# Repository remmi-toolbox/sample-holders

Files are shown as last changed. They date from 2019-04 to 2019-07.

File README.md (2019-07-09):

# About sample-holders
This contains 3D print files for mouse brain holders of various sizes. Additional files for other types of tissue and phantom holders may be added in the near future. Designs were created by Dong Kyu Kim (dong.kyu.kim@vanderbilt.edu) and Mark Does (mark.does@vanderbilt.edu). Work is supported by NIH R01EB019980.

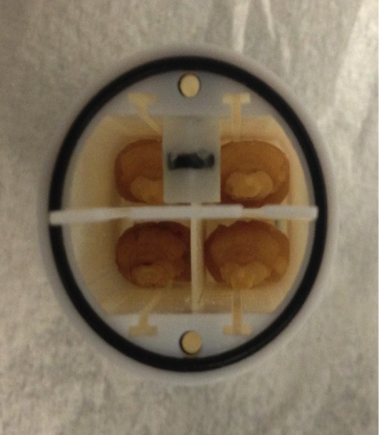
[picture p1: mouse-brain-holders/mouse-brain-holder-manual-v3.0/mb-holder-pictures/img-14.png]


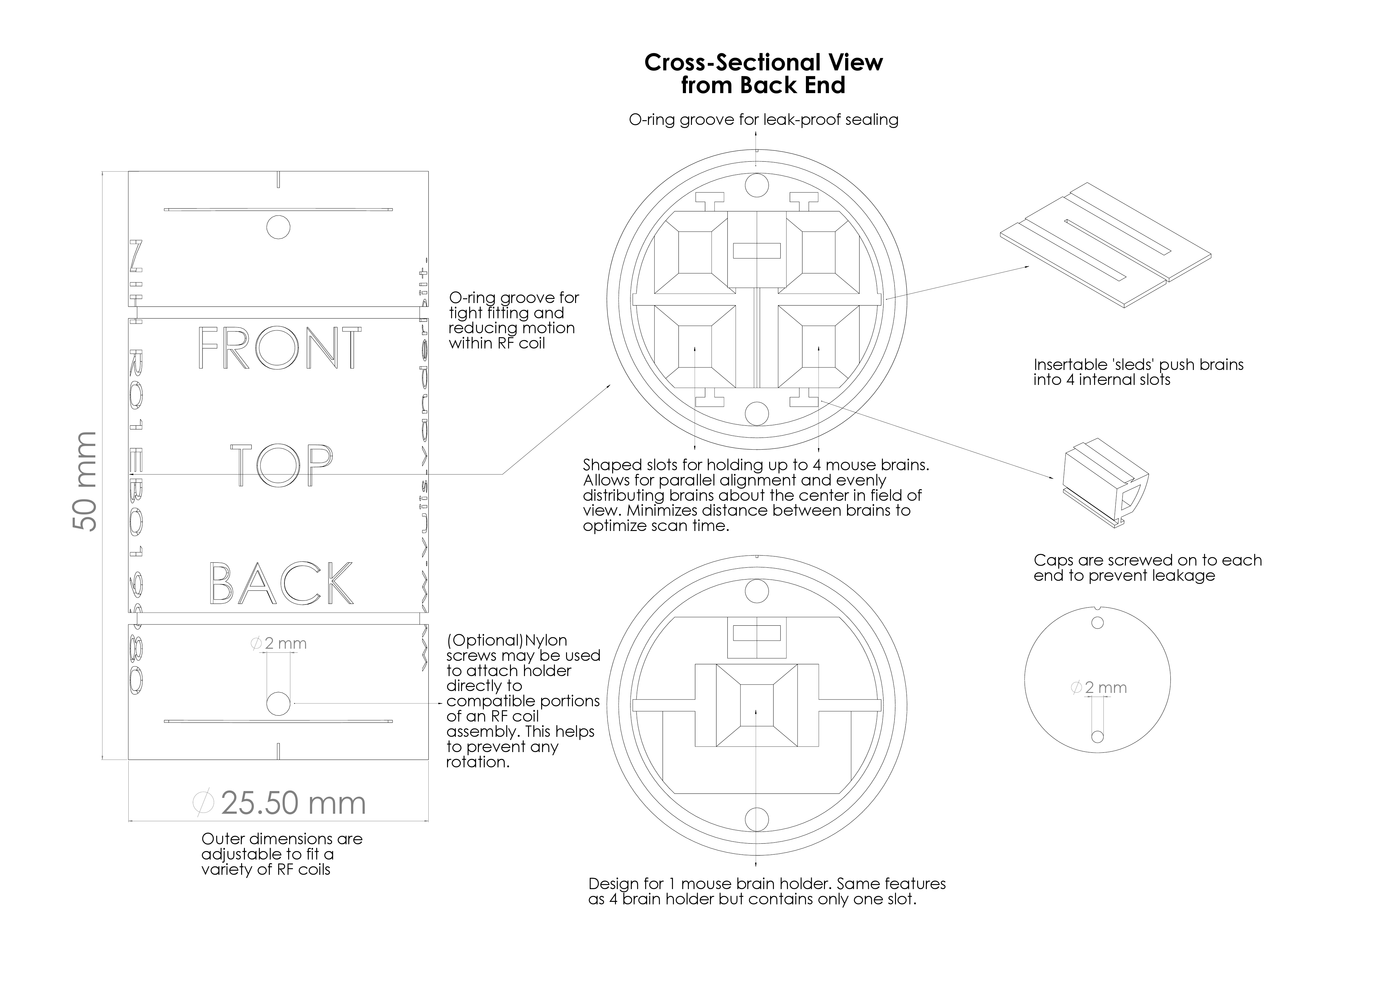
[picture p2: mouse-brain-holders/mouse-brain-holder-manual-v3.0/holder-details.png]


# File Organization

3D print files are organized in the following manner: Type of holder (i.e. mouse brain holder)/ Outer diameter of holder (i.e. 25mm)/ Maximum number of samples that can be held within the holder (i.e. 4-mouse-brain)/ sldprt (SolidWorks Part) and stl (stereolithography) files

Alternatively, if you know what type of holder you are looking for, use the table below to be taken to the appropriate link:

|      |1-mouse-brain   |4-mouse-brain   |6-mouse-brain   |
|:---|---|---|---|
|**20mm**   |[20mm-1mb](/../../tree/master/mouse-brain-holders/20mm/1-mouse-brain)      |               |               |
|**25mm**   |[25mm-1mb](/../../tree/master/mouse-brain-holders/25mm/1-mouse-brain)        |[25mm-4mb](/../../tree/master/mouse-brain-holders/25mm/4-mouse-brain)        |               |
|**35mm**   |[35mm-1mb](/../../tree/master/mouse-brain-holders/35mm/1-mouse-brain)        |[35mm-4mb](/../../tree/master/mouse-brain-holders/35mm/4-mouse-brain)        |[35mm-6mb](/../../tree/master/mouse-brain-holders/35mm/6-mouse-brain)        |
|**38mm**   |[38mm-1mb](/../../tree/master/mouse-brain-holders/38mm/1-mouse-brain)        |[38mm-4mb](/../../tree/master/mouse-brain-holders/38mm/4-mouse-brain)        |[38mm-6mb](/../../tree/master/mouse-brain-holders/38mm/6-mouse-brain)        |
|**40mm**   |[40mm-1mb](/../../tree/master/mouse-brain-holders/40mm/1-mouse-brain)        |[40mm-4mb](/../../tree/master/mouse-brain-holders/40mm/4-mouse-brain)        |[40mm-6mb](/../../tree/master/mouse-brain-holders/40mm/6-mouse-brain)        |

# Usage

3D print designs (.sldprt) can be edited with SolidWorks 2017 and above. The .stl files can be used to directly print each design on an appropriate 3D printer. Recommended 3D print resolution is 29 micron layers (750x750x890 DPI (xyz)). These designs have been tested with a ProJet 3500 HDMax printing in Ultra High Definition (UHD) mode. This level of resolution may be necessary to accurately print small internal features.

Navigate to the desired holder (i.e. mouse-brain-holders/25mm/1-mouse-brain) and view the README for a list of parts to print. Additional parts like O-rings and nylon screws may need to be purchased separately. Links to these parts are on the README. The 3D prints are designed to be compatible with these additional parts.

View the appropriate [**README manual**](/../../tree/master/mouse-brain-holders/mouse-brain-holder-manual-v3.0) (i.e. mouse-brain-holders/mouse-brain-holder-manual/README) for information on holder assembly and usage.

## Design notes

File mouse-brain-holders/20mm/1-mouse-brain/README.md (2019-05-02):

## 1 Mouse Brain Holder for 20mm ID RF Coil

Parts List:

* [2x O-rings (10mmID, 12.6 OD)](https://www.mcmaster.com/1302n124)
* 2x cap\-20mm\-1mb
* 1x holder\-20mm\-1mb
* 1x sled\-20mm\-1mb

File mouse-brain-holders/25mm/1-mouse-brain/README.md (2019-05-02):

## 1 Mouse Brain Holder for 25mm ID RF Coil

Parts List:

* [2x O-rings](https://www.mcmaster.com/9262k194) (21.5mm ID, 23.5mm OD)
* [4x Nylon Screws](https://www.mcmaster.com/92492a705) (M2 x 0.4mm thread)
* [4x Nylon Hex Nuts](https://www.mcmaster.com/93800a300) (M2 x 0.4mm thread)
* 2x cap\-20mm\-1mb
* 1x holder\-20mm\-1mb
* 1x sled\-20mm\-1mb

Optional:

* 2x O-rings to serve as spacers, place on outer groove (ID 24mm, groove width 0.7mm), required O-ring outer diameter will vary based on exact dimensions of the printed object and ID of RF coil
* [2x Nylon Screws](https://www.mcmaster.com/92492a705) for the 2 screw holes at the top of holder, use to situate holder on the coil itself (M2 x 0.4mm thread)
*  [2x Nylon Hex Nuts](https://www.mcmaster.com/93800a300) (M2 x 0.4mm thread)

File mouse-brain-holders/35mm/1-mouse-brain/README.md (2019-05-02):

## 1 Mouse Brain Holder for 35mm ID RF coil

Parts List:

* [2x O-rings](https://www.mcmaster.com/9262k646) (25mm ID, 28mm OD)
* [8x Nylon Screws](https://www.mcmaster.com/92492a707) (M2 x 0.4mm thread)
* [8x Nylon Hex Nuts](https://www.mcmaster.com/93800a300) (M2 x 0.4mm thread) 
* 2x cap\-35mm\-1mb
* 1x holder\-35mm\-1mb
* 1x sled\-35mm\-1mb

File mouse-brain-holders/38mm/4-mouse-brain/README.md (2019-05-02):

## 4 Mouse Brain Holder for 38mm ID RF coil

Parts List:

* [2x O-rings](https://www.mcmaster.com/9262k646) (25mm ID, 28mm OD) 
* [8x Nylon Screws](https://www.mcmaster.com/92492a707) (M2 x 0.4mm thread)
* [8x Nylon Hex Nuts](https://www.mcmaster.com/93800a300) (M2 x 0.4mm thread)
* 2x cap\-38mm\-4mb
* 1x holder\-38mm\-4mb
* 1x separator\-38mm\-4mb
* 2x sled\-38mm\-4mb

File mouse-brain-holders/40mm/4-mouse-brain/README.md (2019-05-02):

## 4 Mouse Brain Holder for 40mm ID RF coil

Parts List:

* [2x O-rings](https://www.mcmaster.com/9262k646) (25mm ID, 28mm OD)
* [8x Nylon Screws](https://www.mcmaster.com/92492a707) (M2 x 0.4mm thread)
* [8x Nylon Hex Nuts](https://www.mcmaster.com/93800a300) (M2 x 0.4mm thread)
* 2x cap\-40mm\-4mb
* 1x holder\-40mm\-4mb
* 1x separator\-40mm\-4mb
* 2x sled\-40mm\-4mb

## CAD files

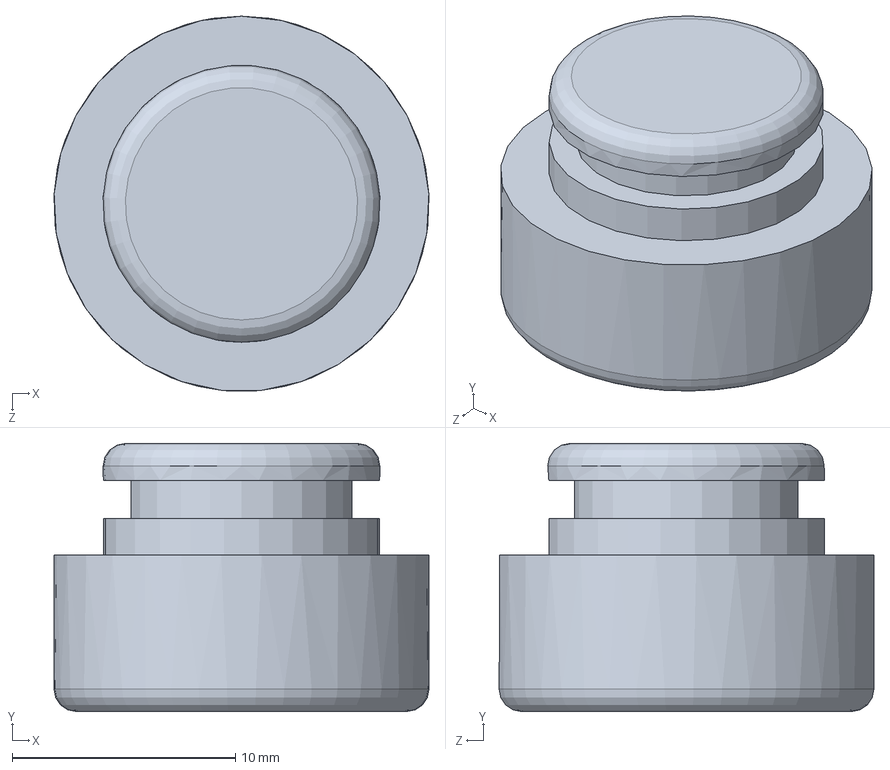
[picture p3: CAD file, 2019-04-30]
mouse-brain-holders/20mm/1-mouse-brain/sldprt/cap-20mm-1mb.SLDPRT
16.8 x 12.0 x 16.8 mm

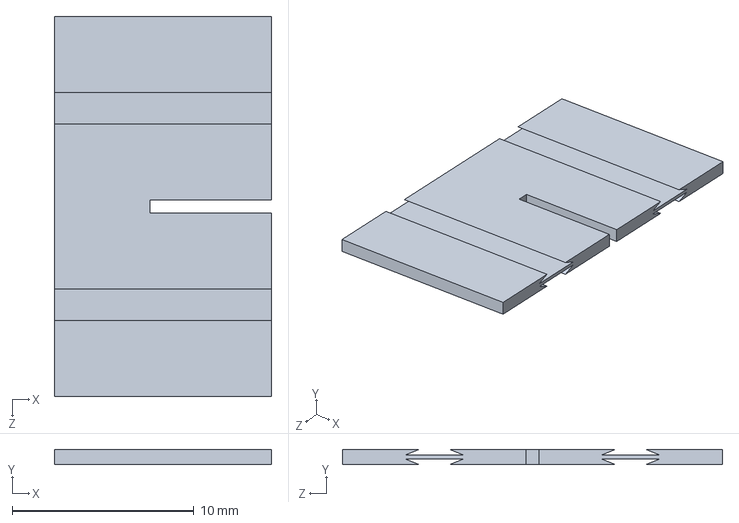
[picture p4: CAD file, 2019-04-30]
mouse-brain-holders/25mm/1-mouse-brain/sldprt/sled-25mm-1mb.SLDPRT
12.0 x 0.8 x 20.9 mm

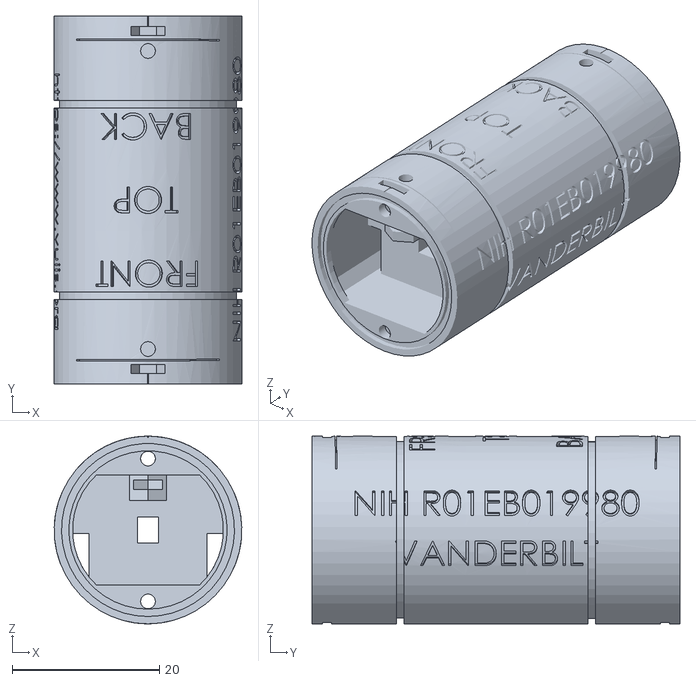
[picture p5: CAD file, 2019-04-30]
mouse-brain-holders/25mm/1-mouse-brain/stl/holder-25mm-1mb.STL
25.5 x 50.0 x 25.5

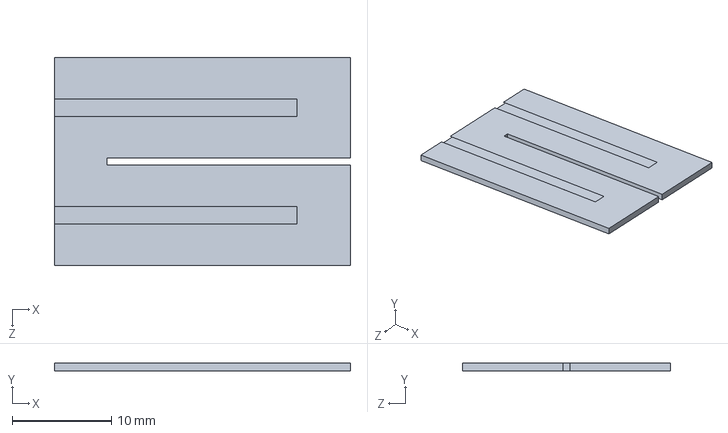
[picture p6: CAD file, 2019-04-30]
mouse-brain-holders/25mm/4-mouse-brain/sldprt/separator-25mm-4mb.SLDPRT
29.8 x 0.8 x 20.9 mm

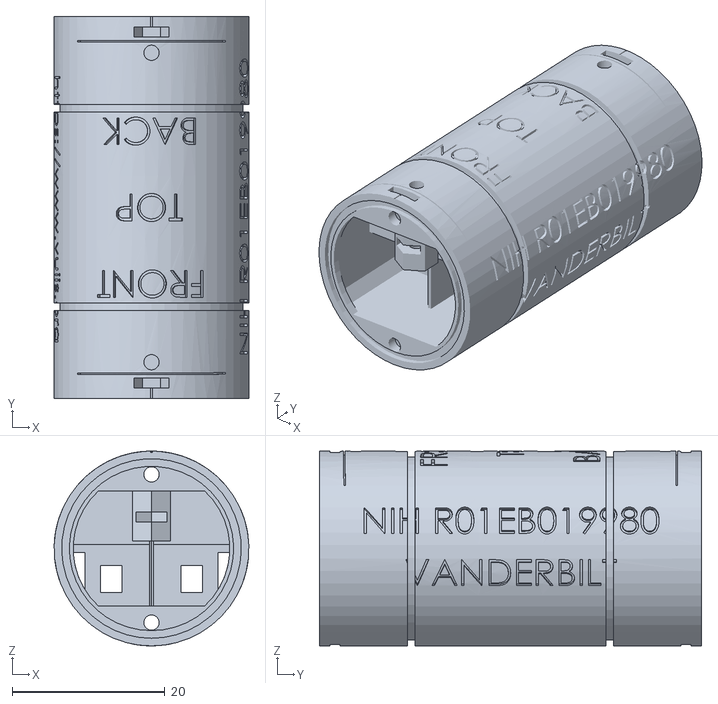
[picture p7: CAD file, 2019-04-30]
mouse-brain-holders/25mm/4-mouse-brain/stl/holder-25mm-4mb.STL
25.5 x 50.0 x 25.5

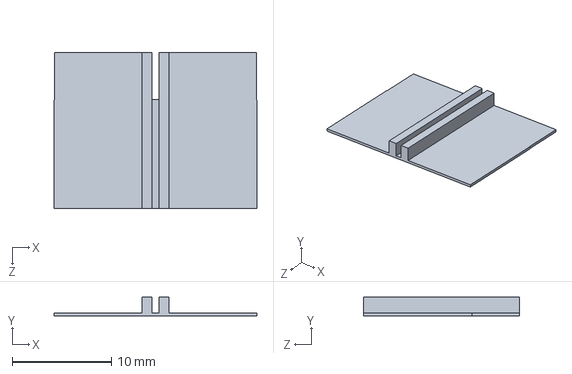
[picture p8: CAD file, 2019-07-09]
mouse-brain-holders/35mm/1-mouse-brain/sldprt/sled-35mm-1mb.SLDPRT
20.5 x 1.90 x 15.8 mm

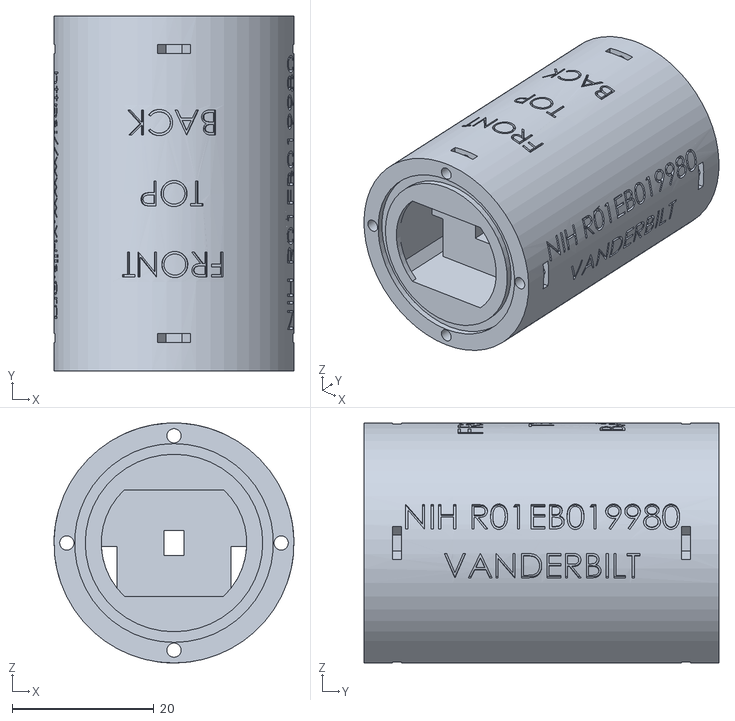
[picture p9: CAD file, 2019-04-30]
mouse-brain-holders/35mm/1-mouse-brain/stl/holder-35mm-1mb.STL
33.8 x 50.0 x 33.8

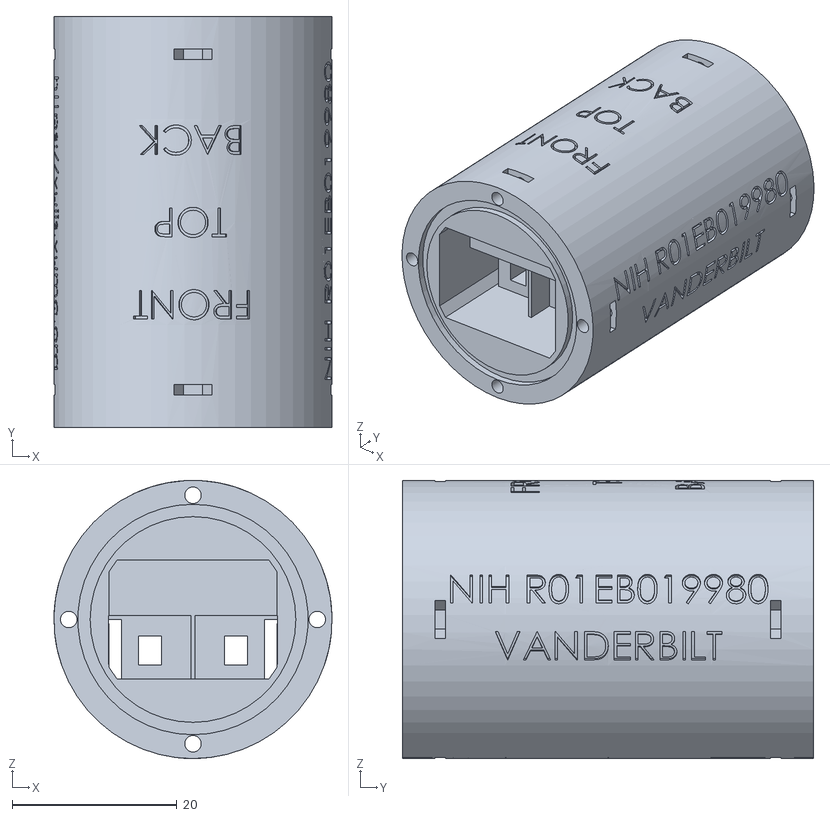
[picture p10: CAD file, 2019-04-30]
mouse-brain-holders/35mm/4-mouse-brain/stl/holder-35mm-4mb.STL
33.8 x 50.0 x 33.8

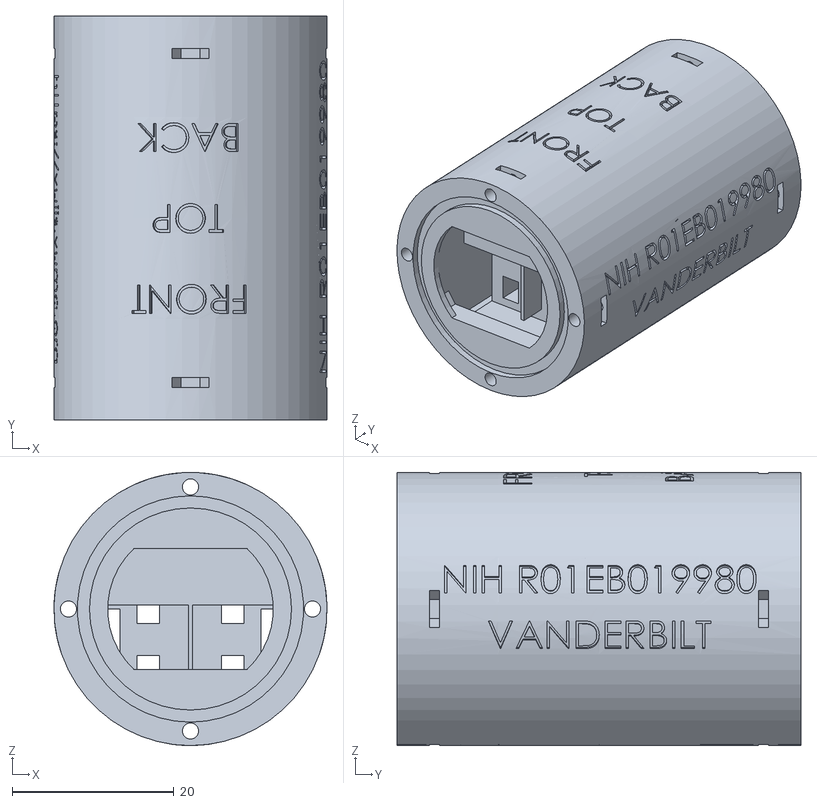
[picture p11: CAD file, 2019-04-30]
mouse-brain-holders/35mm/6-mouse-brain/stl/holder-35mm-6mb.STL
33.8 x 50.0 x 33.8

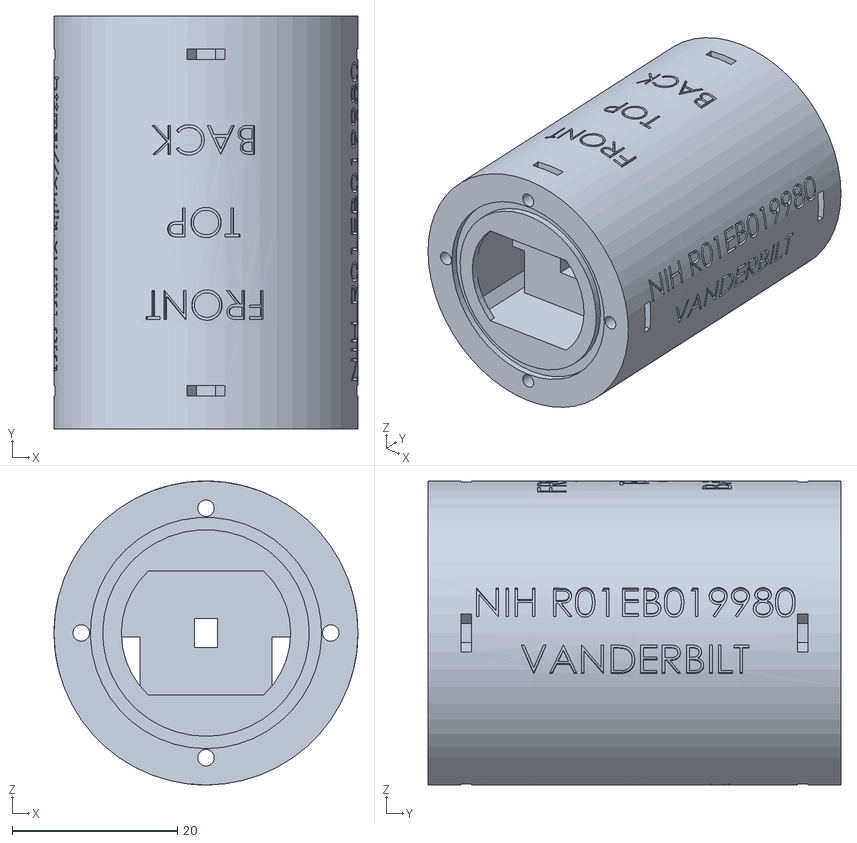
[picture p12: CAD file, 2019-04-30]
mouse-brain-holders/38mm/1-mouse-brain/stl/holder-38mm-1mb.STL
36.8 x 50.0 x 36.8

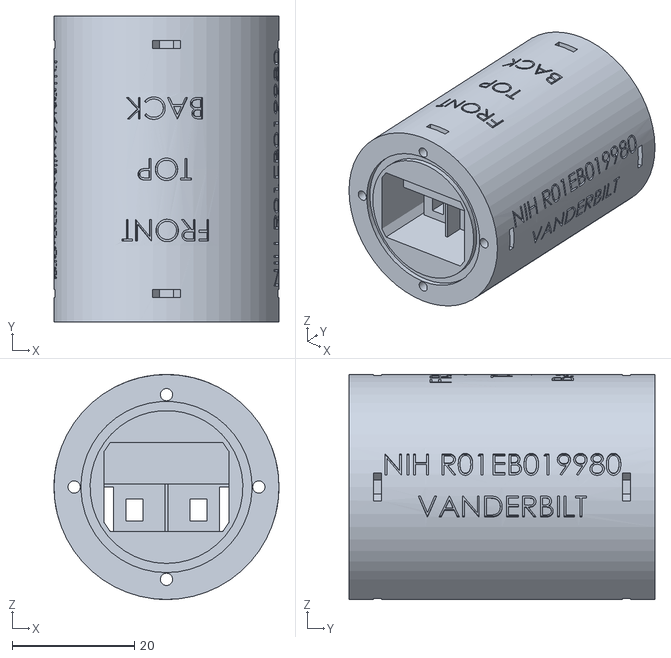
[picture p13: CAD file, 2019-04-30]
mouse-brain-holders/38mm/4-mouse-brain/stl/holder-38mm-4mb.STL
36.8 x 50.0 x 36.8

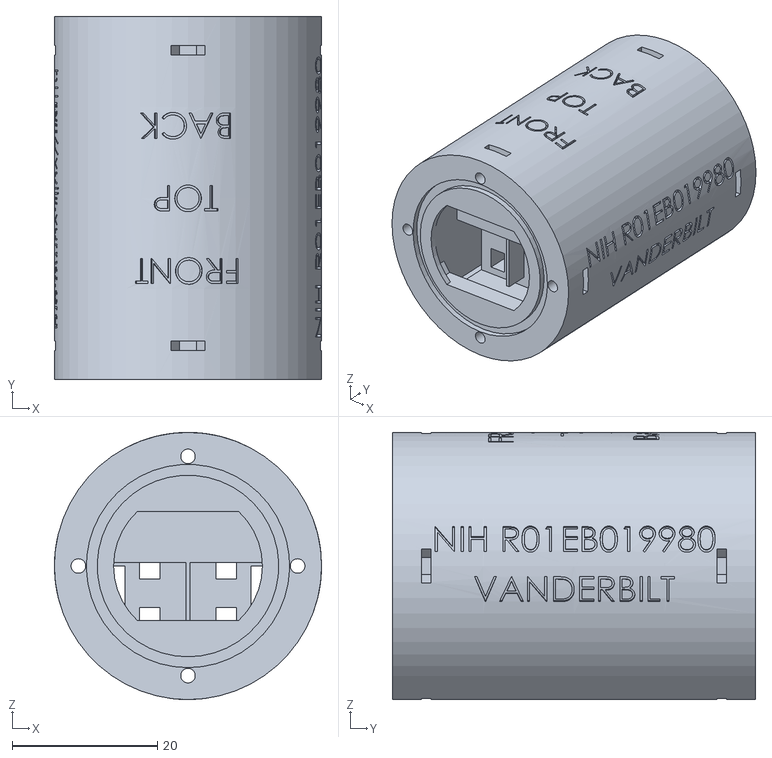
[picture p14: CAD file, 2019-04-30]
mouse-brain-holders/38mm/6-mouse-brain/stl/holder-38mm-6mb.STL
36.8 x 50.0 x 36.8

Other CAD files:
mouse-brain-holders/20mm/1-mouse-brain/sldprt/holder-20mm-1mb.SLDPRT
mouse-brain-holders/20mm/1-mouse-brain/sldprt/sled-20mm-1mb.SLDPRT
mouse-brain-holders/20mm/1-mouse-brain/stl/cap-20mm-1mb.STL
mouse-brain-holders/20mm/1-mouse-brain/stl/holder-20mm-1mb.STL
mouse-brain-holders/20mm/1-mouse-brain/stl/sled-20mm-1mb.STL
mouse-brain-holders/25mm/1-mouse-brain/sldprt/cap-25mm-1mb.SLDPRT
mouse-brain-holders/25mm/1-mouse-brain/stl/cap-25mm-1mb.STL
mouse-brain-holders/25mm/1-mouse-brain/stl/sled-25mm-1mb.STL
mouse-brain-holders/25mm/4-mouse-brain/sldprt/sled-25mm-4mb.SLDPRT
mouse-brain-holders/25mm/4-mouse-brain/stl/separator-25mm-4mb.STL
mouse-brain-holders/25mm/4-mouse-brain/stl/sled-25mm-4mb.STL
mouse-brain-holders/35mm/1-mouse-brain/stl/cap-35mm-1mb.STL
mouse-brain-holders/35mm/1-mouse-brain/stl/sled-35mm-1mb.STL
mouse-brain-holders/35mm/4-mouse-brain/sldprt/cap-35mm-4mb.SLDPRT
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

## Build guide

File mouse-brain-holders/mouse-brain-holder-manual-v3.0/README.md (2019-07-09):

# Mouse Brain Holder Manual v3.0
**By Dong Kyu Kim, dong.kyu.kim@vanderbilt.edu  
PI: Dr. Mark D. Does  
Supported by NIH R01EB019980  
[REMMI Project](https://vuiis.vumc.org/remmi/remmi.php)    
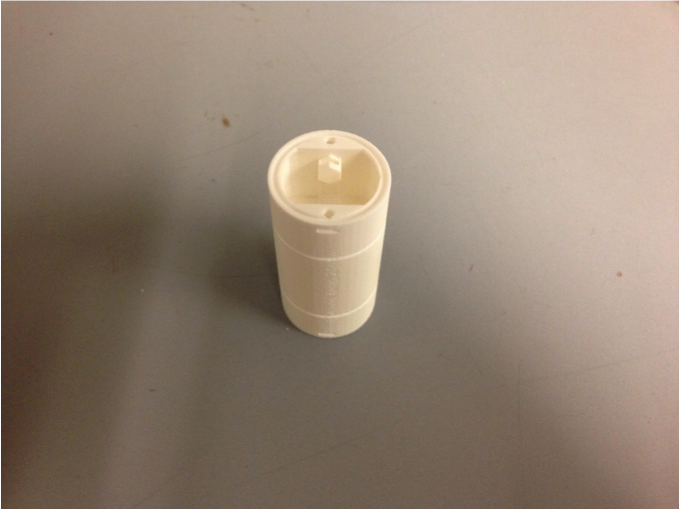
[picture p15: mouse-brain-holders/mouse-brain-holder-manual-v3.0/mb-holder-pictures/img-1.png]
Vanderbilt University and Vanderbilt University Institute of Imaging Science (VUIIS)** 

This MRI compatible 3D printed holder can hold up to 4 mouse brains. Designs are available for 20mm, 25mm, 35mm, 38mm, and 40mm coils in SolidWorks (.sldprt) file format. This manual will use pictures of the 4 mouse brain 25mm holder to describe the preparation procedure. The same procedure is used to prepare the other holders.

## Table of Contents
[Parts List](#parts-list)  
[Holder Printing and Washing](#holder-printing-and-washing)  
[Holder Orientation](#holder-orientation)  
[O-ring and Hex Nut Placement](#o-ring-and-hex-nut-placement)  
[Air Bubble Trapping](#air-bubble-trapping)  
[Capping](#capping)  
[Holder Preparation](#holder-preparation)  
[Tight Fitting](#tight-fitting)  

## Parts List
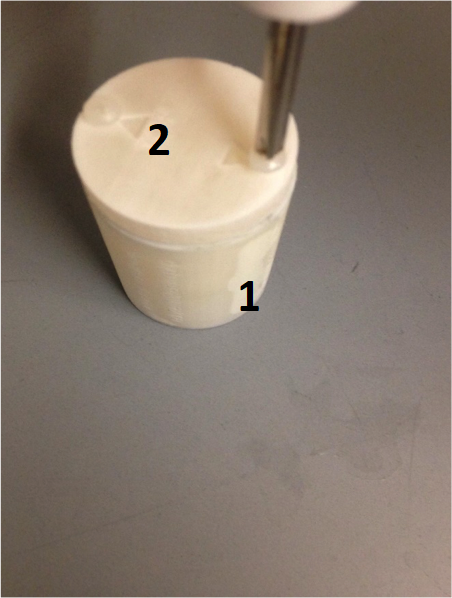
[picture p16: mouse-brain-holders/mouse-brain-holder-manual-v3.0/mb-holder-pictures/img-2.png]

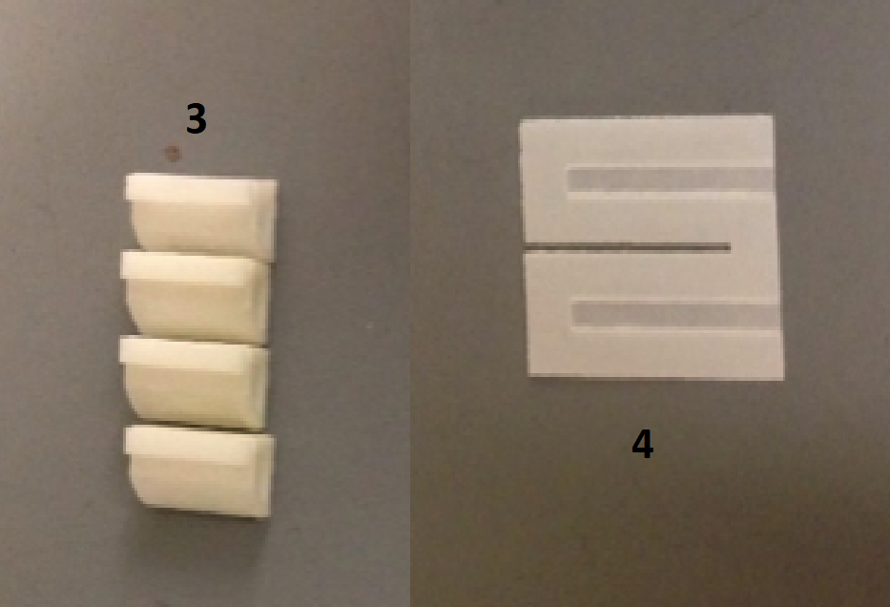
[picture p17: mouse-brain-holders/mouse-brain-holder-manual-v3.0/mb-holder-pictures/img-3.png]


3D printed parts are highlighted in **bold text** throughout the manual. Parts were printed with 3D systems Projet 3500 HDMax at UHD mode with VisiJet M3 Crystal material. Required parts are written in a separate Markdown file for each different type of mouse brain holder. Here we show the required parts for a 4 mouse brain holder for 25mm inner diameter (ID) RF coil:

1. 1x **Holder**
2. 2x **Cap**
3. 4x **Sled**
4. 1x **Separator**
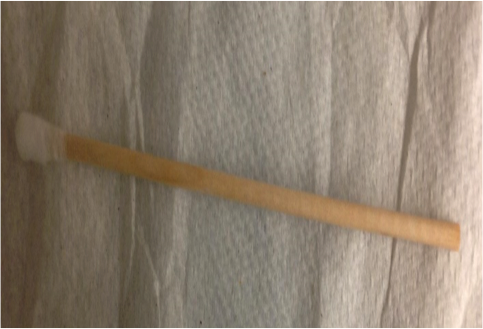
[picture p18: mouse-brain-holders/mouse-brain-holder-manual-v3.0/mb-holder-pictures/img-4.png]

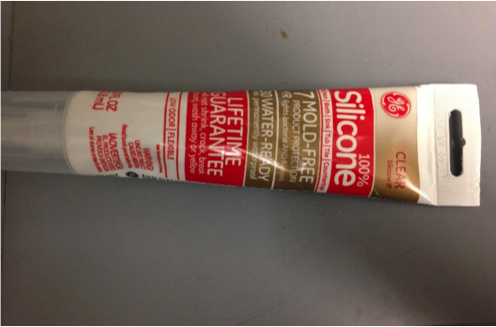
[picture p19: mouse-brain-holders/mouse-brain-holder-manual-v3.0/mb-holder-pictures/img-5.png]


A long Q-tip is recommended for pushing mouse brains in and out of the holder. 100% silicone is required for sealing certain features of the holder where potential leakage may occur.

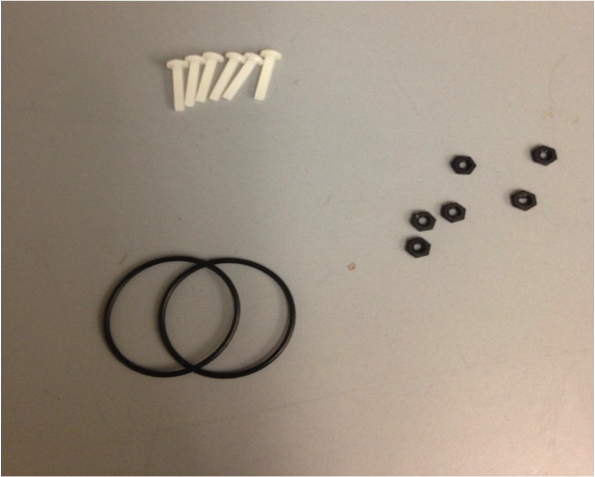
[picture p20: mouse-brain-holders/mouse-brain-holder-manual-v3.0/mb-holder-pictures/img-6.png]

Misc. Parts from McMaster-Carr:  
See Github README files for parts list and where to acquire O-rings, nylon hex nuts, and nylon screws.

## Holder Printing and Washing
3D printing should be done in UHD mode on Projet 3500 HDMax or a printer capable of achieving similar resolution (34x34x29 µm) to ensure proper printing of fine features. After printing, parts should be placed in oven at 62°C for minimum of 3 hours to melt off support material. A heated ultrasonic cleaner filled with mineral oil should be used to remove residual support material in fine spaces in the holder. 1 hour in 62°C oil bath is sufficient. Rinse off oil with soap and water thoroughly and let dry for 1 hour.  [A thin bristle set](https://www.mcmaster.com/7396T71) should be used to scrape through small features in the holder, particularly O-ring grooves and screw holes. Place all parts in a glass jar filled with hexane, ensuring that the parts are fully submerged. Leave in hexane for 1 day. Take parts out and use bristles again to scrape through the holder. Leave to dry for 1 hour. Parts should now be ready to use for scanning.

## Holder Orientation
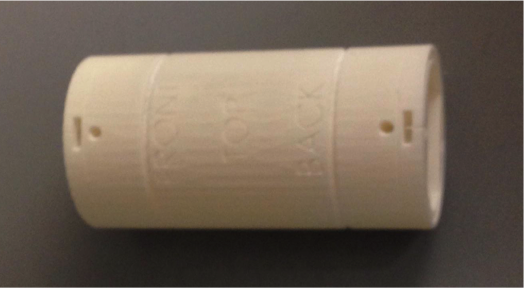
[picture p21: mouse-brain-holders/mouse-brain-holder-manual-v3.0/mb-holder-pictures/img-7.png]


See text on **Holder** to determine the correct orientation. The "FRONT" side goes into the magnet first. The "TOP" side must face the ceiling.

## O-ring and Hex Nut Placement
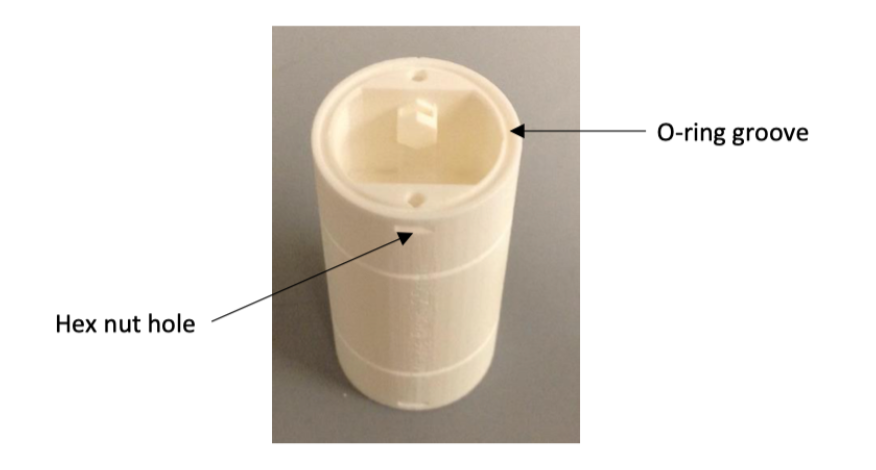
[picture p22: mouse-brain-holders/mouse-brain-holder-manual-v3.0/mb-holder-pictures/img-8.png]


Left: Place the O-ring in the “FRONT” and “BACK” groove of the **Holder**. Firmly press down evenly around the ring and remove any kinks. This is important for preventing fluid leakage.  
Right: Place the hex nuts in the grooves of the **Holder**. There are 4 hex nut holes on the outer surface of the holder (2 in front, 2 in back). Place the hex nuts in so that the flat edge of the nut faces the outward. There are 2 hex nut holes in the interior of the holder (1 in each end). Place the hex nut in appropriately and **seal these holes with a layer of silicone.**

## Air Bubble Trapping
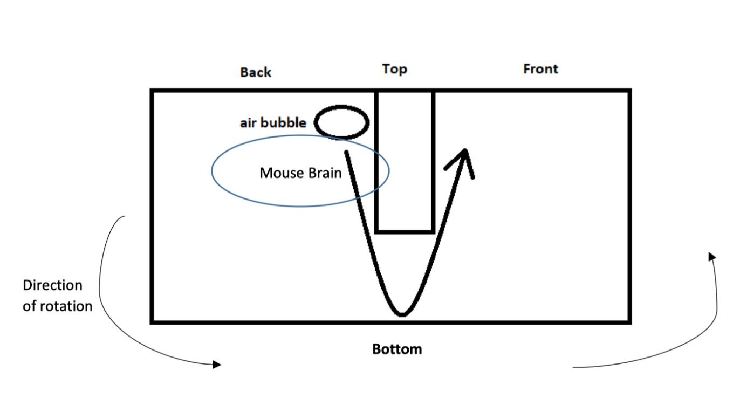
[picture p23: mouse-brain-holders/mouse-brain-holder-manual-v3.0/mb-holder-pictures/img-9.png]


Undesirable air bubbles within the **Holder** can be trapped away from mouse brains by rotating the holder 360°. Start with the “BACK” end facing the ceiling, then rotate to the “BOTTOM” facing up, then “FRONT” end, then “TOP” facing the ceiling.

## Capping
While screwing in the cap, apply some downward pressure on the cap with your thumb to ensure proper O-ring sealing between the cap and the holder surfaces.

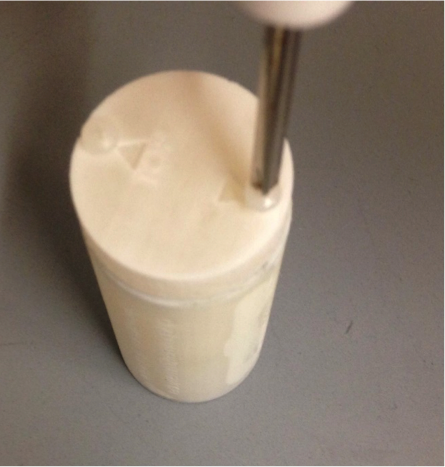
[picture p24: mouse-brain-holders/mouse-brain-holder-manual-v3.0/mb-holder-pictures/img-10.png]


## Holder Preparation
Start with capping the "FRONT" end of the holder.  
Brains should insert such that the frontal lobe of the brain inserts first. The top of the brain should be facing the “TOP” of the holder. Insert brains from the “BACK” end, and push toward the “FRONT” end. The interior of the holder has 4 shaped grooves that help to align the brains parallel to the length of the holder.

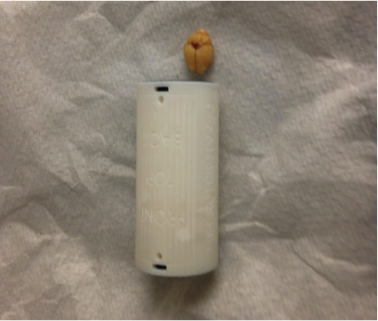
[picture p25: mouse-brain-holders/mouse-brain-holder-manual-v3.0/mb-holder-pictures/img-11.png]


Start by inserting two brains at the “BOTTOM” of the holder. Use a long q-tip to help guide the brains down. You may need to rotate the brains a little initially to get them into the holder.

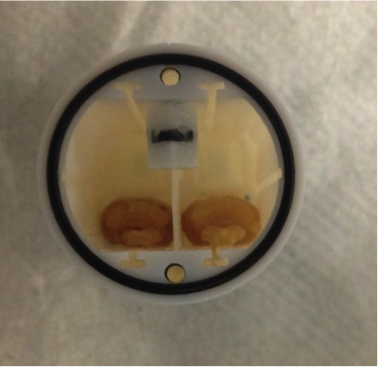
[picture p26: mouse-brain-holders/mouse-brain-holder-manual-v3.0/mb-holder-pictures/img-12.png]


Insert the remaining two brains at the “TOP” of the holder, again using a long q-tip to guide the brains down. Ensure the four brains are all aligned parallel along the length of the holder.

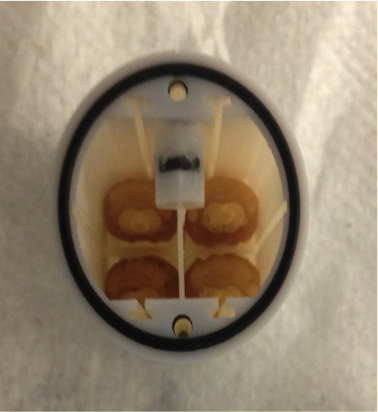
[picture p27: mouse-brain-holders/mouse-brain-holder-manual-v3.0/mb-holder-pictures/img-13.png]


Insert **Separator** in the middle groove all the way until it cannot be pushed further. For all designs, the **Separator** serves to separate adjacent rows of compartments.

  

Insert **Sled** in the T-shaped grooves and the trapezoidal grooves in the middle sled. For some designs, the **Sled** is a flat piece kind of like the separator, but all sleds serve to keep the brains situated in the middle of the holder. Use the grooves as guides to move the sled down until it is flush up against the mouse brain. Pipette imaging solution of choice (i.e. Fomblin) until the holder is completely filled with the solution.

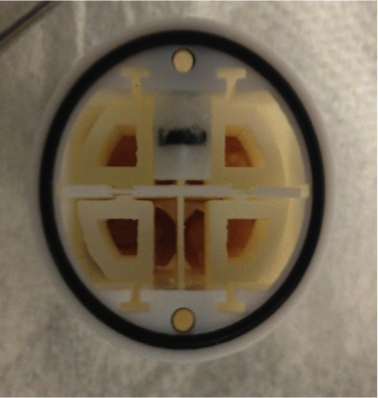
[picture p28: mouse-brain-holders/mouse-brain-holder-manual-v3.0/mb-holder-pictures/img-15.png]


Screw on cap on the “BACK” end, again applying downward pressure on the cap while screwing. If the holder leaks at this point, silicone may be applied at the interface between the cap and holder.

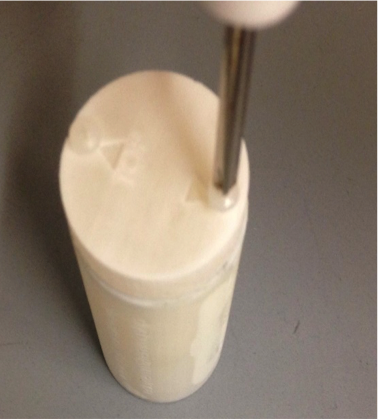
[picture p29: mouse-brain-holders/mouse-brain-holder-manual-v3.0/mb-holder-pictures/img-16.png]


## Tight Fitting
This design features additional O-ring grooves on the outer surface that can help facilitate tighter fitting within the RF coil. The exact dimensions of the O-ring will vary depending on RF coil diameter and dimensional tolerances. Alternatively, a few wounds of tape can be used instead to fill any gaps between the holder and RF coil.

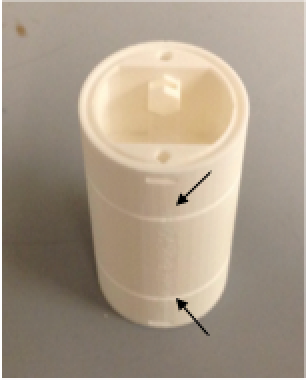
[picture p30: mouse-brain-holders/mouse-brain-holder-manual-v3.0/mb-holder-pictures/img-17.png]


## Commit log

2019-05-02 renamed files
    [cap-20mm-1mb.SLDPRT, cap-20mm-1mb.STL, cap-25mm-1mb.SLDPRT, cap-25mm-1mb.STL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]
2019-05-03 renamed folders
    [cap-25mm-1mb.SLDPRT, cap-25mm-1mb.STL, holder-25mm-1mb.STL, sled-25mm-1mb.SLDPRT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]
2019-05-03 renamed folder
    [cap-25mm-1mb.SLDPRT, cap-25mm-1mb.STL, holder-25mm-1mb.STL, sled-25mm-1mb.SLDPRT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]
2019-07-09 edited sled files for 35, 38, and 40mm coil
    [sled-35mm-1mb.SLDPRT, sled-35mm-1mb.STL, sled-35mm-4mb.SLDPRT, sled-35mm-4mb.STL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]
